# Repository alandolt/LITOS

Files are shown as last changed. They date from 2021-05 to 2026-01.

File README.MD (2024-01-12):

# LITOS - **L**ed **I**llumination **T**ool for **O**ptogenetic **S**timulation

**For more information or if you need any help, please contact us at litosforscience[at]outlook.com.**

The **L**ed **I**llumination **T**ool for **O**ptogenetic **S**timulation (**LITOS**) can be used for the stimulation of cells containing an optogenetic system. A commercially available 32x64 RGB LED matrix is used to illuminate cells placed in various microplate formats (6 well up to 96 wells), petri dishes or cell culture flasks. The control unit for the LED matrix is a custom-built printed circuit board (PCB) containing a screen which shows relevant information during the illumination process. 

During LITOS development, we deliberately focused on user-friendliness. LITOS can be ordered pre-built, thus no complicated assembly process is required. Individual stimulation patterns can be first created in a spreadsheet application, like Microsoft Excel, then they are loaded to LITOS over an easy-to-use interface, accessible as a website hosted on the device itself. Thus, no knowledge of a programming language is needed, and the device can even be operated by nontechnical oriented users. 

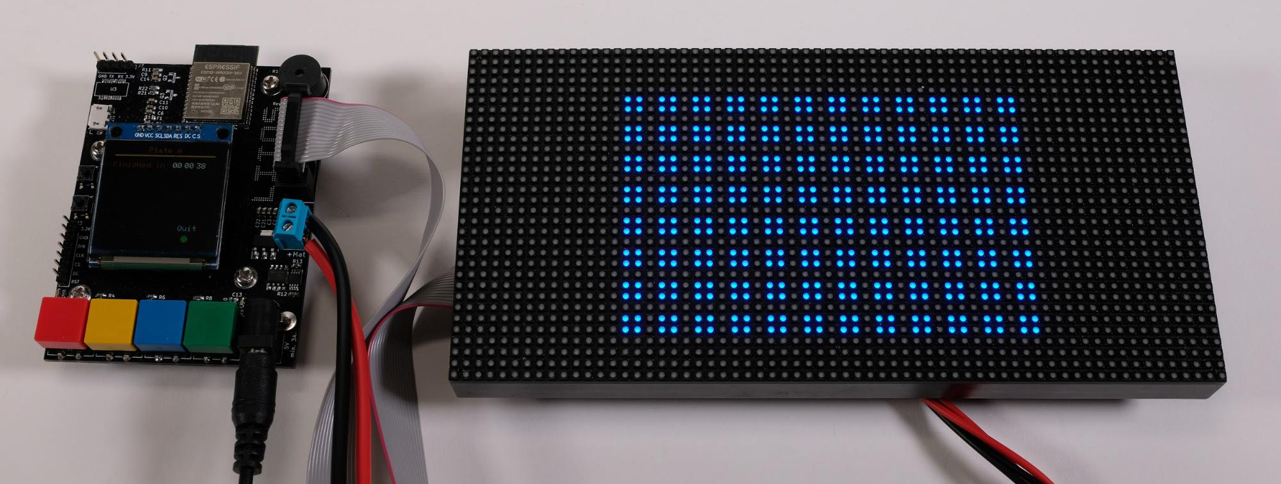
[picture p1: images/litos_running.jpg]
LITOS

*LITOS, an easy-to-use system for optogenetic stimulation*

## Why another device for optogenetic stimulation
Optogenetic methods are powerful tools to assess complex signalling pathways with a high spatial-temporal resolution. However, there is a lack of adequate instrumentation to exploit these methods allowing high-throughput automated experiments. While available commercial devices are often too expensive, published solutions requires programming knowledge or have a complicated assembly process. We presents therefore LITOS, a new emerging tool to render optogenetic methods even accessible to labs with a small budget or non-technical user. Thanks to the easy-to-use–interface no knowledge of a programming language is needed, whereas it is still possible to program complex stimulation patterns. Despite being delivered pre-assembled, LITOS remains significantly cheaper than most of the published and commercially available solutions, costing only $ 150. By using a LED matrix as illumination source, even petri-dishes or cell culture flasks can be stimulated in addition to different formats of microtiter plates.

## Features 
- Easy-to-use graphical user interface to change stimulation patterns for optogenetic experiments. No programming knowledge is required. 
- Stimulation patterns are provided as spreadsheet files (MS Excel, LibreOffice Calc)
- It comes pre-assembled. Neither a 3D printer, nor soldering are required before you can start your experiments. 
- Cells can be placed in well plates (96, 48, 24, 12), petri dishes, or cell culture flasks. 
- Very affordable, only about $150 per device. 

## Getting started

To learn more about LITOS, please read our [paper, published 2022 in scientific reports](https://www.nature.com/articles/s41598-022-17312-x), consult our [github wiki](../../wiki) or checkout the [LITOS - First steps](https://youtu.be/o76gi3OUZvs) video.

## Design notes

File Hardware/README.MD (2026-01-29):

# LITOS Hardware
In case you want to order LITOS directly from a PCB manufacturing service, the folder [*PCB design data*](PCB%20design%20data) contains the needed information (Gerbers file with PCB position file, schematics, and bill of material). Additionally, you can find the raw KiCad PCB layout project under [*LITOS Kicad Rev4.3.zip*](PCB%20design%20data/LITOS%20Kicad%20Rev4.3.zip). 

For the proper alignment of the microtiter plate on the LED matrix the blueprints (for building them with a 3D printer or a CNC machine) for two different masks (one / two microplates) are provided under [*Alignment masks*](Alignment%20masks). The mask for one microplate allows its placement in the middle of the LED matrix, whereas the mask for two plates stocks them horizontally. This allows to stimulate two multiwell plates with one LITOS to further increase through-put. Please note that when using the mask for two plates, the first and last row cannot be illuminated. 

An optional 3D printed case that protects LITOS can be found in the [*3D printed case*](3D%20printed%20case) folder. The case comes in two versions, with or without ventilation holes. Albeit, given that LITOS does not heat up excessively, you can use whichever version you prefer. To minimize overhangs, we recommend you print the case in the orientation it is stored in the .stl file, the open side of the case facing the printer plate. To adjust for under- or overextruding printers, changing the scale of the whole design worked well for us (98%-102%). No support structures were needed with our printer (Creality CR 20 Pro).

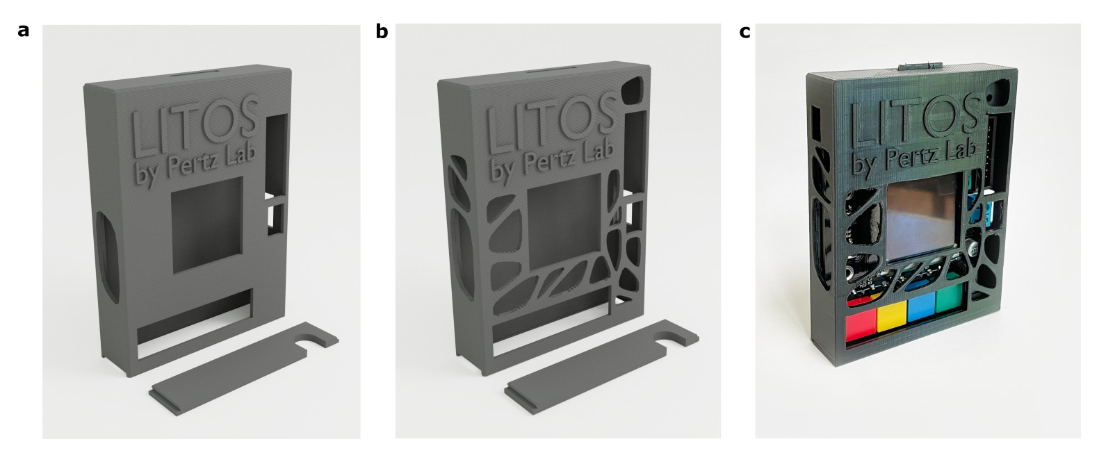
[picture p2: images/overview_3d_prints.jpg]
a) closed design, b) desgin with ventilation holes, c) photo of printed case with ventilation holes


<br>

> **Warning** By default, the source code adapted for revision 4 is used during the programming process. When you are still using an older revision 3 board, you can choose the adapted source code for this version by selecting LITOS_Rev2_Rev3 as build environment in PlatformIO. 

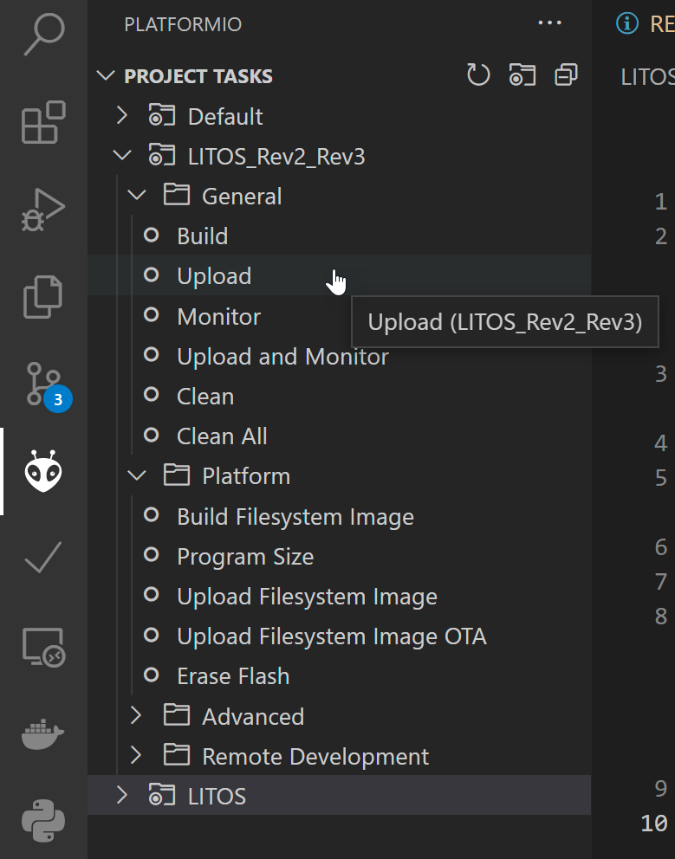
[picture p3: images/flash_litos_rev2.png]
Chose the build environment LITOS_Rev2_Rev3 when you still use an old Rev2 or Rev3 LITOS, else you can directly choose LITOS as build environment


*Chose the build environment LITOS_Rev2_Rev3 when you still use an old Rev2 or Rev3 LITOS, else you can directly choose LITOS as build environment.*

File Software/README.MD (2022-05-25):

# LITOS software

In this folder, you find all the needed files to flash your own LITOS device. For more information check our [wiki](../../../wiki/3.-Setting-up-LITOS'-software).

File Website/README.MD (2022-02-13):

# LITOS configuration website
In this folder, you find the source code of LITOS configuration website. It is based on the [vue-admin-template](https://github.com/PanJiaChen/vue-admin-template) project, which itself is based on [vue.js](https://vuejs.org/). 
After compiling of the JavaScript code, the HTML file is zipped and converted in a C++ file to be served from PROGMEM by the [ESPAsyncWebServer](https://github.com/me-no-dev/ESPAsyncWebServer). 
However, albeit the configuration on LITOS is working without problem, it is currently not possible to compile it by the files provided in this folder, as there is a problem with an outdated dependency. 
We are currently in the process of fixing the error and provide you as soon as possible with an updated, working website version, that you then also can compile yourself.

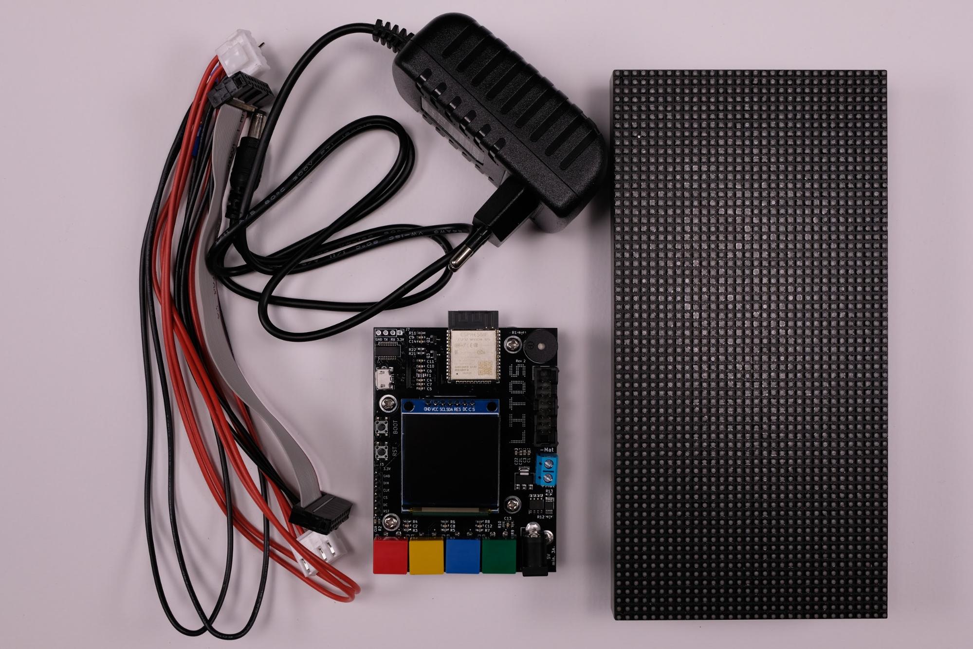
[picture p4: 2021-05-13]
images/litos_overview.jpg

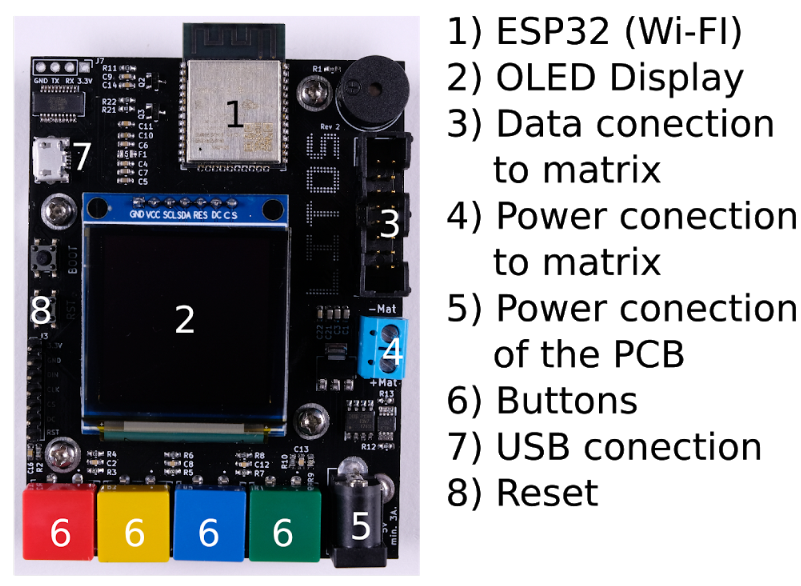
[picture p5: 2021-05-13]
images/pcb_overview.png

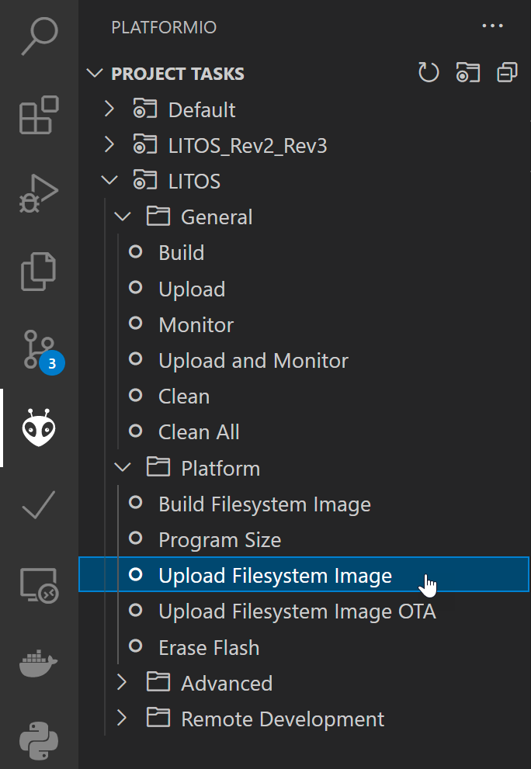
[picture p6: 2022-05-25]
images/flash_file_system.png

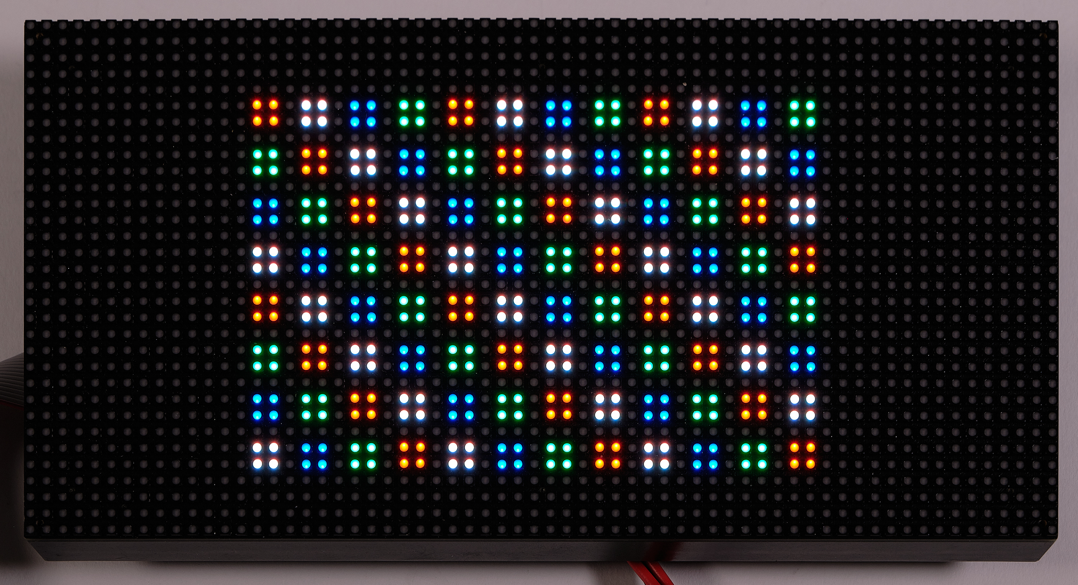
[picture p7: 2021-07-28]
images/LITOS_Muster_3.jpg

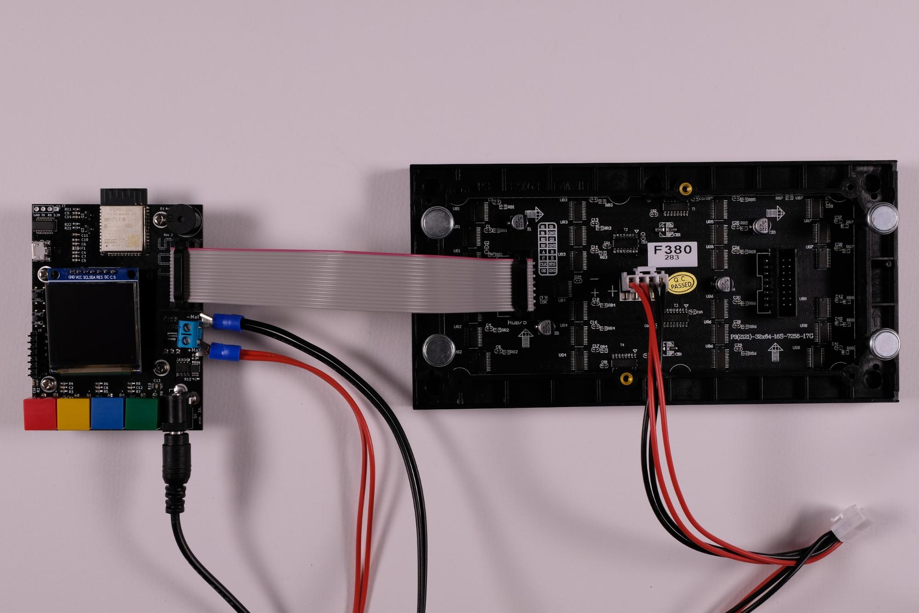
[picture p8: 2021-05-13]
images/litos_back.jpg

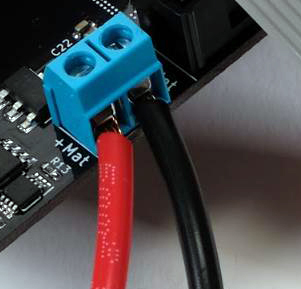
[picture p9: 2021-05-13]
images/power_connector.jpg

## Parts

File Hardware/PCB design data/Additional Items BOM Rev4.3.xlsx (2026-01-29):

LITOS REV 4.3
Additional items
For the BOM please see the .csv, here are only the additionally required items.
Item | Qty | Reference(s) | Value/ Type | Package | Mouser No | Mfr. No | Manufacturer | Description
~~1~~ | ~~1~~ | ~~for SW 3~~ | ~~Switch Cap~~ |  | ~~653-B32-1380 ~~ | ~~B32-1380 ~~ | ~~Omron Electronics ~~ | ~~Switch Bezels / Switch Caps 12MM X 12MM RED CAP ~~
~~2~~ | ~~1~~ | ~~for SW 4~~ | ~~Switch Cap~~ |  | ~~653-B32-1330 ~~ | ~~B32-1330 ~~ | ~~Omron Electronics ~~ | ~~Switch Bezels / Switch Caps 12X12 KEYCAP YELLOW ~~
~~3~~ | ~~1~~ | ~~for SW 5~~ | ~~Switch Cap~~ |  | ~~653-B32-1340 ~~ | ~~B32-1340 ~~ | ~~Omron Electronics ~~ | ~~Switch Bezels / Switch Caps 12X12 KEYCAP BLUE ~~
~~4~~ | ~~1~~ | ~~for SW 6~~ | ~~Switch Cap~~ |  | ~~653-B32-1350 ~~ | ~~B32-1350 ~~ | ~~Omron Electronics ~~ | ~~Switch Bezels / Switch Caps Green 12x12 mm Key Top ~~
 |  | As mouser has the required item not in stock, here another source for all keycaps (all 4 colors included). You can order a 60sets6color set, containing enough keycaps for up to 15 LITOS Rev 4. You can also take keycaps from a local supplier of your choice, the aliexpress links here serves only as a reference. If ordering the keycaps greatly extends the turnaround time (more than 3 days), do not bother to order them and thus ignore position 1-4. Further, if you order from aliexpress, do not put the transparent covers on top of the keycaps. Thanks |  |  |  |  |  | https://www.aliexpress.com/item/32845173329.html?pdp_ext_f=%7B%22sku_id%22%3A%2265174878652%22%7D
5 | 1 | will be mounted on J4 through male/female header interaction | OLED Display Module |  |  |  |  | 1.5 Inch OLED 128x128 Display Color LCD Screen SSD1351 with 2.54mm male headers already soldered in place from your local supplier, for ex. Banggood (currently not in stock, so please see below)
 |  |  |  |  |  |  |  | https://www.banggood.com/1_5-Inch-OLED-128x128-Display-Color-LCD-Screen-SSD1351-Color-OLED-p-1640372.html?rmmds=search&cur_warehouse=CN
 |  |  |  |  |  |  |  | or diymore (or any other local supplier)
 |  |  |  |  |  |  |  | https://aliexpress.com/item/4000380926640.html
 |  |  |  |  |  |  |  | Important: Headers must be already soldered
 |  |  |  |  |  |  |  | also important: you must not take this version of this display (https://www.waveshare.com/wiki/1.5inch_RGB_OLED_Module (as no male headers are present)

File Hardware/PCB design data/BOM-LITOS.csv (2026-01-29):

Comment | Designator | Footprint | LCSC | Quantity
0.1uF | C16,C4,C6 | C_0603_1608Metric_Pad1.05x0.95mm_HandSolder | C14663 | 3
0.1uF/50V | C14,C22,C9 | C_0603_1608Metric_Pad1.05x0.95mm_HandSolder | C14663 | 3
0R | R1,R16 | R_0603_1608Metric_Pad1.05x0.95mm_HandSolder | C21189 | 2
100uF | C1 | CP_Elec_6.3x5.4 | C3001238 | 1
10k | R10,R11,R12,R2,R21,R22,R4,R6,R8 | R_0603_1608Metric_Pad1.05x0.95mm_HandSolder | C25804 | 9
10nF | C12,C13,C2,C8 | C_0603_1608Metric_Pad1.05x0.95mm_HandSolder | C57112 | 4
1k | R3,R5,R7,R9 | R_0603_1608Metric_Pad1.05x0.95mm_HandSolder | C21190 | 4
22uF/10V | C21,C3 | C_0603_1608Metric_Pad1.05x0.95mm_HandSolder | C59461 | 2
4.7k | R13 | R_0603_1608Metric_Pad1.05x0.95mm_HandSolder | C23162 | 1
4.7uF | C10 | C_0603_1608Metric_Pad1.05x0.95mm_HandSolder | C19666 | 1
5.11k | R14,R15 | R_0603_1608Metric_Pad1.05x0.95mm_HandSolder | C23186 | 2
AMS1117-3.3 | U1 | SOT-223-3_TabPin2 | C6186 | 1
B3F-4050 | SW3,SW4,SW5,SW6 | B3F-4050 | C86707 | 4
BSS138PW,115 | Q1 | SOT-323-3_L2.2-W1.3-P1.30-LS2.1-BL | C193366 | 1
Barrel_Jack_MountingPin | J1 | DC-005-5A-2.0 | C381116 | 1
Buzzer | BZ1 | BUZ-SMD_4P-L8.5-W8.5-TL | C189207 | 1
CH340C | U3 | CH340C | C84681 | 1
ESP32-WROOM-32E | U2 | ESP32-WROOM-32E | C701342 | 1
HUB_75 | J2 | B-3000S16P-0110 | C132430 | 1
IRF7416TRPBF | Q4 | IRF7416TRPBF | C3000 | 1
Oled_display_SSD1351_module | J4 | PinSocket_1x07_P2.54mm_Vertical | C2886701 | 1
SS8050-G | Q2,Q3 | SS8050-G | C2150 | 2
SW_Push | SW1,SW2 | PTS647SN50SMTR2LFS | C2799414 | 2
Screw_Terminal_01x02 | J5 | CONN-TH_2P-P7.62_L15.2-W16.7-EX4.2 | C496127 | 1
USB_C_Receptacle_USB2.0 | J6 | USB-C-SMD_MC-311D | C136423 | 1
LOGO | G*** | logo_litos |  | 1

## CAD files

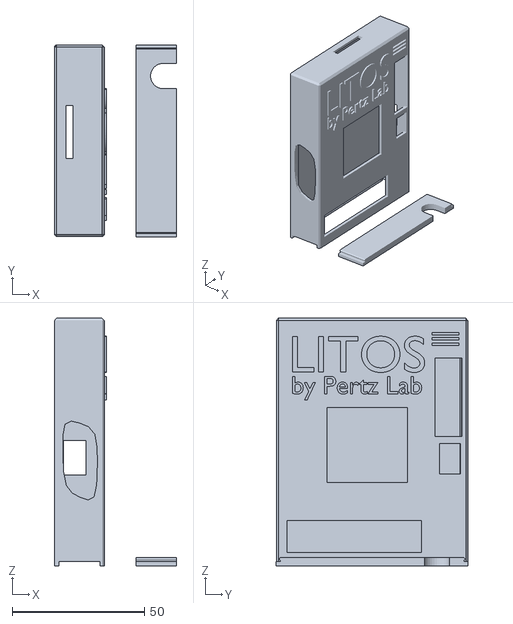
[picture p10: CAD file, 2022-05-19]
Hardware/3D printed case/LITOS_case_rev_4_solid.stl
46.2 x 72.6 x 93.9

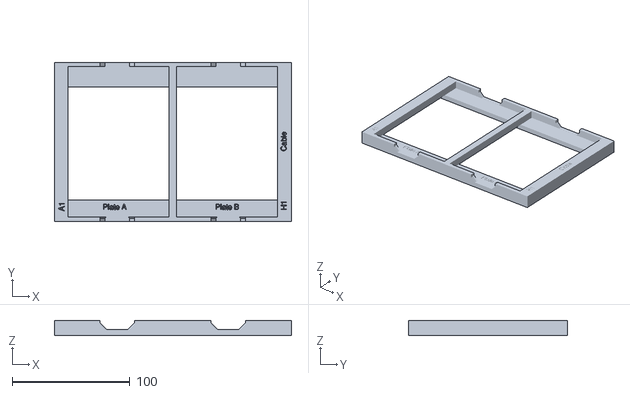
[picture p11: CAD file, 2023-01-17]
Hardware/Alignment masks/mask_two_wellplate.stl
201.6 x 135.2 x 12.4

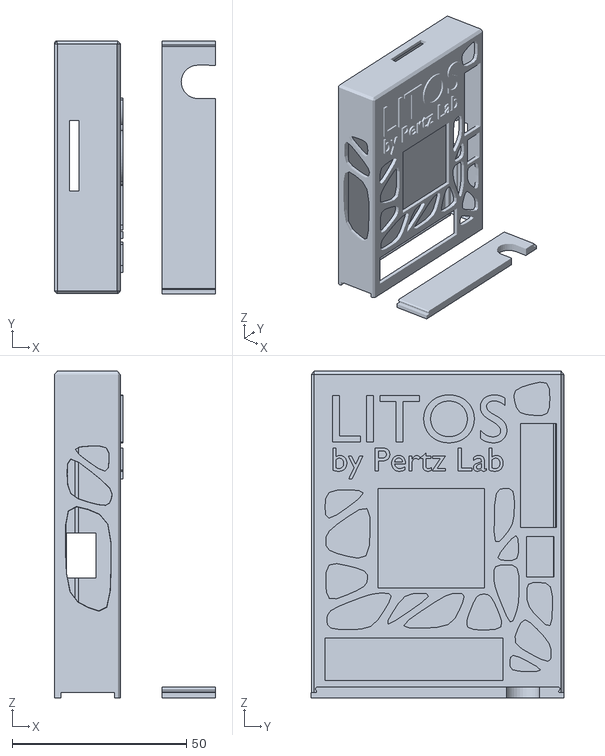
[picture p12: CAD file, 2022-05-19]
Hardware/3D printed case/LITOS_case_rev_4_vents.stl
46.2 x 72.6 x 93.9

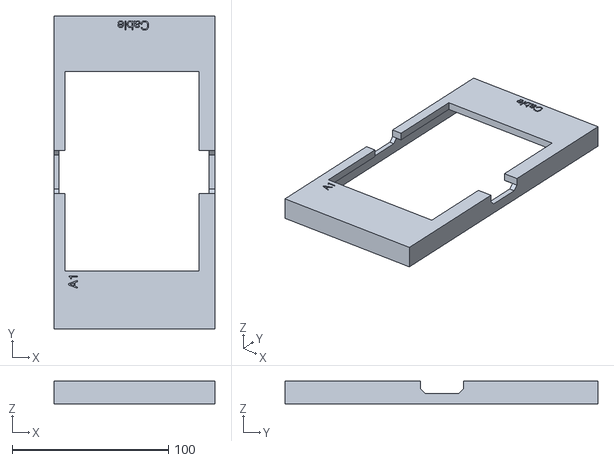
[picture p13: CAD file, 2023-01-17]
Hardware/Alignment masks/mask_one_wellplate.stl
103.1 x 200.2 x 14.7

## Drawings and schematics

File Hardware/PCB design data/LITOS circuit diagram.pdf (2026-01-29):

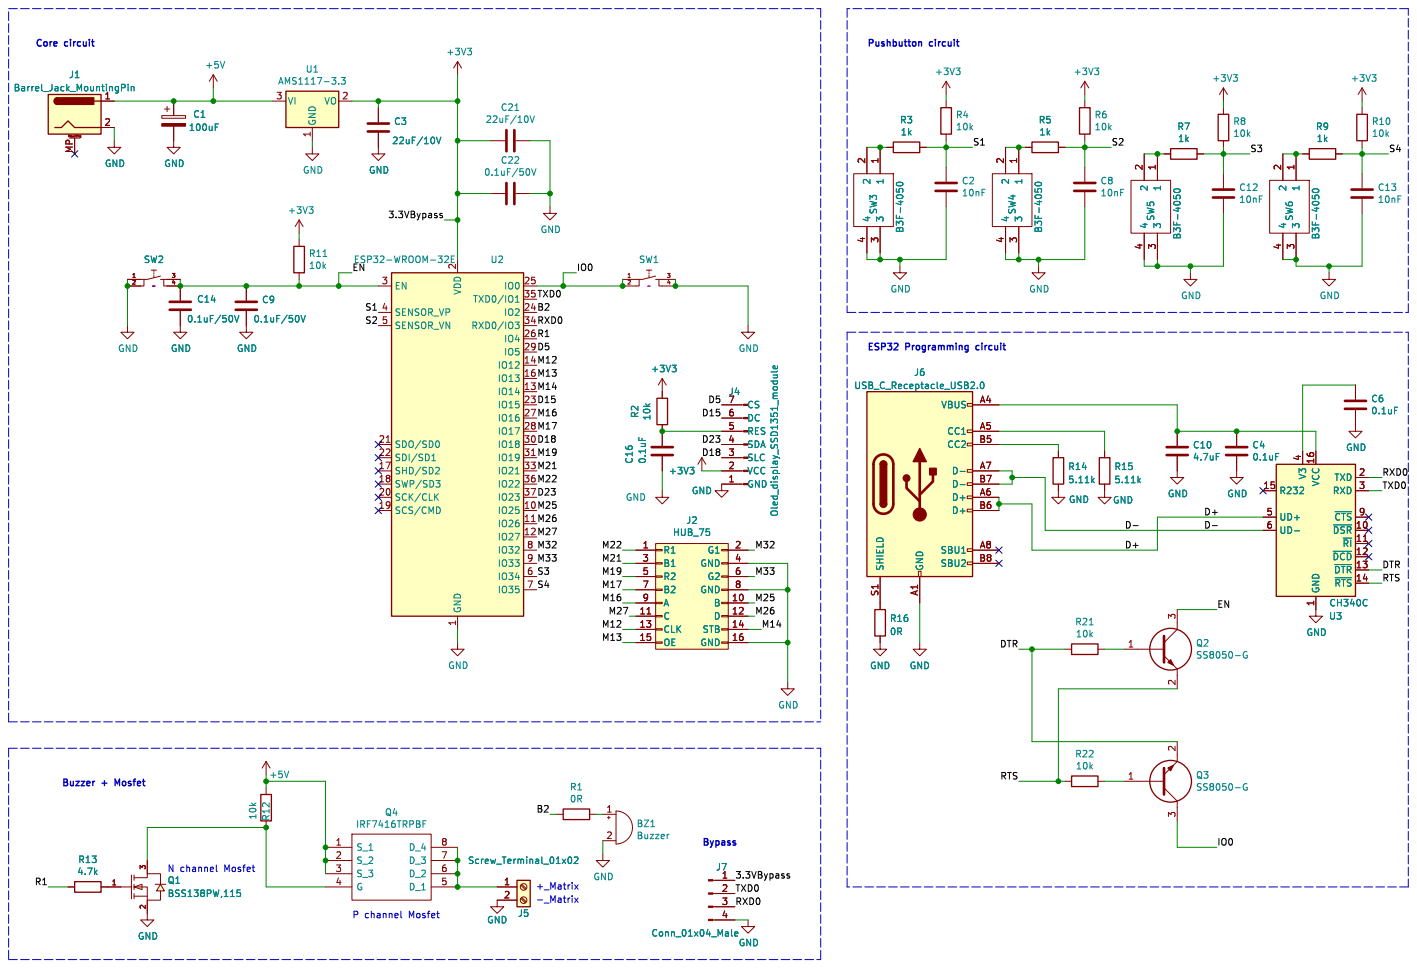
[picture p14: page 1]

1 TXD 2 RXD 3 ~{CTS}9 ~{DSR} 10 ~{RI} 11 ~{DCD} 12 ~{DTR} 13 ~{RTS} 14 GND

1 TXD 2 RXD 3 ~{CTS}9 ~{DSR} 10 ~{RI} 11 ~{DCD} 12 ~{DTR} 13 ~{RTS} 14 U3CH340C

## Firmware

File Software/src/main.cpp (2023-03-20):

/**
 * @file main.cpp
 * @author Alex Landolt
 * @brief Main.cpp file of LITOS, here all the sub librarys and function will be invoked and included. Contains void setup and loop
 * @version 0.3
 * @date 2020-05-25
 */

#include <Arduino.h>
#include <SPIFFS.h>

#include "save_restore_config.h"
#include "wifi_webserver.h"
#include "wellplate.h"
#include "matrix.h"
#include "display.h"
#include "button.h"
#include "buzzer.h"

unsigned long int current_time;
const unsigned long refresh_intervall = 100;
unsigned long last_refresh_time = 0;
bool two_plates_enabled = false;

void setup()
{
	init_matrix_power();
	delay(100);
	Serial.begin(115200);
	SPIFFS.begin(); /// open file system

	config.load_configuration();
	Serial.println(config.get_con_mode());
	Serial.println(config.get_ssid());
	Serial.println(config.get_wlan_password());
	init_wlan();
	delay(100);
	init_webserver();
	delay(200);
	init_display();
	delay(200);
	init_matrix();
	delay(100);

	buzzer.init_buzzer();
	plate_A.wellplate_setup();
	if (config.get_last_wellplate('A') > 100)
	{
		plate_B.wellplate_setup();
		two_plates_enabled = true;
	}
}
void loop()
{
	current_time = millis();

	switch (screen)
	{
	case home_screen:
		if (button_1.pressed()) /// both well plates A + B will be started
		{
			screen = status_A_B_screen;
			plate_A.begin(current_time);
			plate_B.begin(current_time);
			draw_status_screen();
		}
		if (button_2.pressed()) /// only A will be started
		{
			screen = status_A_screen;
			plate_A.begin(current_time);
			draw_status_screen();
		}
		if (button_3.pressed()) /// only B will be started
		{
			screen = status_B_screen;
			plate_B.begin(current_time);
			draw_status_screen();
		}
		if (button_4.pressed()) // show test screen where outlines can be marked
		{
			screen = test_screen;
			draw_test_screen();
		}
		break;
	case home_screen_one:
		if (button_2.pressed()) /// only A will be started
		{
			screen = status_A_screen;
			plate_A.begin(current_time);
			draw_status_screen();
		}
		if (button_4.pressed()) // show test screen where outlines can be marked
		{
			screen = test_screen;
			draw_test_screen();
		}
		break;
	case status_A_screen: /// A is currently running
		if (QUIT_ON_RED)
		{
			if (button_1.pressed()) /// abort and go back to home
			{
				plate_A.abort_program();
				screen = home_screen;
				draw_home();
			}
		}
		else
		{
			if (button_4.pressed()) /// abort and go back to home
			{
				plate_A.abort_program();
				screen = home_screen;
				draw_home();
			}
		}
		break;
	case status_B_screen: /// B is currently running
		if (QUIT_ON_RED)
		{
			if (button_1.pressed()) /// abort and go back to home
			{
				plate_B.abort_program();
				screen = home_screen;
				draw_home();
			}
		}
		else
		{
			if (button_4.pressed()) /// abort and go back to home
			{
				plate_B.abort_program();
				screen = home_screen;
				draw_home();
			}
		}
		break;

	case status_A_B_screen: /// A and B are running simultanously
		if (QUIT_ON_RED)
		{
			if (button_1.pressed()) /// abort and go back to home
			{
				plate_A.abort_program();
				plate_A.abort_program();
				screen = home_screen;
				draw_home();
			}
		}
		else
		{
			if (button_4.pressed()) /// abort and go back to home
			{
				plate_A.abort_program();
				plate_A.abort_program();
				screen = home_screen;
				draw_home();
			}
		}
		break;

	case test_screen:
		if (button_1.pressed())
		{
			plate_A.mark_outlines();
			if (two_plates_enabled)
			{
				plate_B.mark_outlines();
			}
		}
		if (button_2.pressed())
		{
			plate_A.mark_well();
			if (two_plates_enabled)
			{
				plate_B.mark_well();
			}
		}
		if (button_4.pressed())
		{
			plate_A.reset_mark();
			plate_B.reset_mark();
			ref_backgroundLayer().clearScreen();
			draw_home();
		}
		break;
	default:
		break;
	}

	if (plate_A.check(current_time) | plate_B.check(current_time)) /// power on / power off Matrix through MOSFET high/low pin
	{
		matrix_on();
	}
	else
	{
		matrix_off();
	}

	if (current_time - last_refresh_time >= refresh_intervall)
	{
		update_status_screen(); /// updates the status screens of the OLED display
		messages.update(current_time);
		buzzer.check_beep(current_time); // check if a beep has been requested by another part of the programm
		last_refresh_time += refresh_intervall;
	}
	dns_server_next_request();
	delay(5);
}

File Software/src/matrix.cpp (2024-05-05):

/**
 * @file matrix.cpp
 * @author Alex Landolt 
 * @brief C file containing functions needed for controlling the LED matrix and the MOSFET
 * @version 0.3
 * @date 2020-05-25
 */
#include "matrix.h"

RGB64x32MatrixPanel_I2S_DMA backgroundLayer;

#define R1 GPIO_NUM_22
#define G1 GPIO_NUM_32
#define BL1 GPIO_NUM_21
#define R2 GPIO_NUM_19
#define G2 GPIO_NUM_33
#define BL2 GPIO_NUM_17

#define CH_A GPIO_NUM_16
#define CH_B GPIO_NUM_25
#define CH_C GPIO_NUM_27
#define CH_D GPIO_NUM_26
#define CH_E -1

#define LAT GPIO_NUM_14
#define OE GPIO_NUM_13
#define CLK GPIO_NUM_12

int sig_data_base = I2S1O_DATA_OUT8_IDX;
int sig_clk = I2S1O_WS_OUT_IDX;
gpio_num_t gpio_pins_def[16] = {R1, G1, BL1, R2, G2, BL2, LAT, OE, CH_A, CH_B, CH_C, CH_D};

const byte led_matrix_mosfet = 4; /// pin where the MOSFET is located
static bool is_matrix_on;

/**
 * @brief Used to generate reference to LED matrix, as so we can control it in the wellplate part of LITOS code
 * 
 * @return RGB64x32MatrixPanel_I2S_DMA&, that is nothing more than a reference to the LED matrix
 */
RGB64x32MatrixPanel_I2S_DMA &ref_backgroundLayer()
{
    return backgroundLayer;
}

/**
 * @brief called in void setup to initialize matrix
 * 
 */
void init_matrix()
{
    //matrix_on();
    digitalWrite(led_matrix_mosfet, HIGH);
    reset_panel();
    digitalWrite(led_matrix_mosfet, LOW);

    backgroundLayer.setPanelBrightness(60);
    backgroundLayer.begin(R1, G1, BL1, R2, G2, BL2, CH_A, CH_B, CH_C, CH_D, CH_E, LAT, OE, CLK);
    digitalWrite(led_matrix_mosfet, HIGH);
    matrix_off(); /// helper function to cut off data lines
}

void init_matrix_power()
{
    pinMode(led_matrix_mosfet, OUTPUT); /// initialize MOSFET pin
    is_matrix_on = true;
    matrix_off();
}

/**
 * @brief helper function to cut off data lines and power through MOSFET and internal pull down resistors 
 * 
 */
void matrix_off()
{
    if (is_matrix_on)
    {
        backgroundLayer.fillScreen(0x0000);
        digitalWrite(led_matrix_mosfet, LOW);
        delay(20);
        sleep_matrix(gpio_pins_def);
        is_matrix_on = false;
    }
}
/**
 * @brief activate matrix by supplying power through internal MOSFET 
 * 
 */
void matrix_on()
{
    if (!is_matrix_on)
    {
        wake_up_matrix(gpio_pins_def);
        digitalWrite(led_matrix_mosfet, HIGH);
        is_matrix_on = true;
    }
}

void gpio_setup_out(gpio_num_t gpio, int sig)
{
    PIN_FUNC_SELECT(GPIO_PIN_MUX_REG[gpio], PIN_FUNC_GPIO);
    gpio_set_direction(gpio, GPIO_MODE_OUTPUT);
    gpio_matrix_out(gpio, sig, false, false);
}

void sleep_matrix(gpio_num_t *gpio_pins)
{
    for (int x = 0; x < 12; x++)
    {
        gpio_setup_out(gpio_pins[x], 0x100);
    }
    gpio_setup_out(CLK, 0x100);
}

void wake_up_matrix(gpio_num_t *gpio_pins)
{
    for (int x = 0; x < 12; x++)
    {
        gpio_setup_out(gpio_pins[x], sig_data_base + x);
    }
    gpio_setup_out(CLK, sig_clk);
}

void reset_panel()
{
    int MaxLed = 64;

    int C12[16] = {0, 1, 1, 1, 1, 1, 1, 1, 1, 1, 1, 1, 1, 1, 1, 1};
    int C13[16] = {0, 0, 0, 0, 0, 0, 0, 0, 0, 1, 0, 0, 0, 0, 0, 0};

    pinMode(R1, OUTPUT);
    pinMode(G1, OUTPUT);
    pinMode(BL1, OUTPUT);
    pinMode(R2, OUTPUT);
    pinMode(G2, OUTPUT);
    pinMode(BL2, OUTPUT);
    pinMode(CH_A, OUTPUT);
    pinMode(CH_B, OUTPUT);
    pinMode(CH_C, OUTPUT);
    pinMode(CH_D, OUTPUT);
    pinMode(CH_E, OUTPUT);
    pinMode(CLK, OUTPUT);
    pinMode(LAT, OUTPUT);
    pinMode(OE, OUTPUT);

    // Send Data to control register 11
    digitalWrite(OE, HIGH); // Display reset
    digitalWrite(LAT, LOW);
    digitalWrite(CLK, LOW);
    for (int l = 0; l < MaxLed; l++)
    {
        int y = l % 16;
        digitalWrite(R1, LOW);
        digitalWrite(G1, LOW);
        digitalWrite(BL1, LOW);
        digitalWrite(R2, LOW);
        digitalWrite(G2, LOW);
        digitalWrite(BL2, LOW);
        if (C12[y] == 1)
        {
            digitalWrite(R1, HIGH);
            digitalWrite(G1, HIGH);
            digitalWrite(BL1, HIGH);
            digitalWrite(R2, HIGH);
            digitalWrite(G2, HIGH);
            digitalWrite(BL2, HIGH);
        }
        if (l > MaxLed - 12)
        {
            digitalWrite(LAT, HIGH);
        }
        else
        {
            digitalWrite(LAT, LOW);
        }
        digitalWrite(CLK, HIGH);
        digitalWrite(CLK, LOW);
    }
    digitalWrite(LAT, LOW);
    digitalWrite(CLK, LOW);
    // Send Data to control register 12
    for (int l = 0; l < MaxLed; l++)
    {
        int y = l % 16;
        digitalWrite(R1, LOW);
        digitalWrite(G1, LOW);
        digitalWrite(BL1, LOW);
        digitalWrite(R2, LOW);
        digitalWrite(G2, LOW);
        digitalWrite(BL2, LOW);
        if (C13[y] == 1)
        {
            digitalWrite(R1, HIGH);
            digitalWrite(G1, HIGH);
            digitalWrite(BL1, HIGH);
            digitalWrite(R2, HIGH);
            digitalWrite(G2, HIGH);
            digitalWrite(BL2, HIGH);
        }
        if (l > MaxLed - 13)
        {
            digitalWrite(LAT, HIGH);
        }
        else
        {
            digitalWrite(LAT, LOW);
        }
        digitalWrite(CLK, HIGH);
        digitalWrite(CLK, LOW);
    }
    digitalWrite(LAT, LOW);
    digitalWrite(CLK, LOW);
}

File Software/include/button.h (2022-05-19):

/**
 * @file button.h
 * @author Alex Landolt
 * @brief Header file for button class. Handles pushbutton with Software debounce through checking them multiple times before triggering an action.
 * @version 0.3
 * @date 2020-05-25
 */

#ifndef BUTTON_H
#define BUTTON_H

#define PIN_BUTTON_1 36
#define PIN_BUTTON_2 39
#define PIN_BUTTON_3 34
#define PIN_BUTTON_4 35

#ifdef LITOS_REV_2
#undef PIN_BUTTON_1
#define PIN_BUTTON_1 35
#undef PIN_BUTTON_2
#define PIN_BUTTON_2 34
#undef PIN_BUTTON_3
#define PIN_BUTTON_3 39
#undef PIN_BUTTON_4
#define PIN_BUTTON_4 36
#endif

#include <Arduino.h>

/**
 * @brief Class to register and handle push button press with Software debounce
 *
 */
class Button
{
private:
    byte _button, _state, _lastState, _reading;
    unsigned int _count;
    unsigned long _delay, _last;
    boolean _wait;
    bool _1st_press;
    void Button_u(byte &button_pin); /// underlaying function used for initialization

public:
    Button(byte button_pin);                      /// constructor to create Button object on specific pin of ESP32
    Button(byte button_pin, unsigned long delay); /// Button object with custom debounce delay

    bool pressed();       /// returns the debounced button state: LOW or HIGH.
    unsigned int count(); /// Returns the number of times the button was pressed.
    void resetCount();    /// Resets the button count number.
};

extern Button button_1; /// Declaration of Buttons 1-4 of LITOS
extern Button button_2;
extern Button button_3;
extern Button button_4;

#endif

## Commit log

2020-04-04 same status as first release, felis silvestris
    [demo.csv]
2020-04-20 rename (remove init_)
    [demo.csv]
2020-04-22 two_wellplates now_working
    [plate_A.csv, plate_B.csv]
2020-05-06 bug fix_websocket crashed in get file list
    [LITOS_proof.csv, MCF10A_Exp1.csv, demo.csv, pertz_lab_Exp2.csv]
2020-07-22 rect circle nun einstellig, Korr webserver, partition
    [no_ota.csv]
2020-09-07 1.3.0: Outline function
    Implementation of an outline function which marks the outlines of a microplate. Additionally the corner wells can be marked to place the microplate correctly on the LED RGB Matrix. Over the website i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
2021-03-15 branch with DMA LED matrix library
    This branch uses the DMA LED matrix from
    https://github.com/mrfaptastic/ESP32-RGB64x32MatrixPanel-I2S-DMA/
    It uses DMA memory instead of heap allocation.
    In theory it uses less CPU.
    As the underlaying API is different (Adafruit GFX instead of smartmatrix), all function calls manipulating the drawn forms in wellplate.cpp and matrix.cpp were changed. Additionally, as the radius is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
2021-07-27 Housekeeping: Addition of README.MD and manual
    [large_spiffs_16MB.csv, no_ota.csv]
2022-02-01 Addition of masks for 3D printer
    [1Plate_cover.dxf, 1Plate_cover_original.dxf, 2Plate_cover.dxf, 2Plate_cover_original.dxf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]
2022-02-02 Move everything to software related to software folder
    [LITOS_proof.csv, MCF10A_Exp1.csv, large_spiffs_16MB.csv, no_ota.csv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]
2022-02-13 Addition of PCB schematics
    [LITOS_v3 BOM.xlsx, LITOS_v3-B_Cu.gbl, LITOS_v3-B_Mask.gbs, LITOS_v3-B_SilkS.gbo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]
2022-03-17 added example patterns
    [Demo.csv, Demo2_loops.csv, Demo3_colors.csv, Demo4_shapes.csv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]
2022-03-17 add new demo file
    [Demo.csv]
2022-03-17 move files to folder example patterns
    [Demo.csv, Demo2_loops.csv, Demo3_colors.csv, Demo4_shapes.csv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]
2022-04-07 Pre-release of hardware revision 4 of LITOS PCB
    - USB flashing error present in rev 3 got fixed
    - Software mostly interchangable between rev 3 and 4.
    - PCB revision gets currently tested
    - For more information, see Redme in hardware folder.
    [LITOS_v3 BOM.xlsx, LITOS_v3-B_Cu.gbl, LITOS_v3-B_Mask.gbs, LITOS_v3-B_SilkS.gbo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]
2022-04-16 Bugfix for PCB Pre-release Rev 4
    - Depending on the micro USB, you have chosen for the assembly, it is possible that the micro USB connector flange is placed on top of the board, instead being feely besides the board. By placing the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
2022-05-13 Compillation did not work anymore on new esp32 core due to ESP32 Async webserver library.
    Fixed by taken this library directly from git repository instead of platformio repo
2022-05-18 Change to espressif32 3.5.0 as rebootloop when flashing with espressif32 4.2.0 framework
2022-05-19 Adapt Platformio.ini and code to be able to compile LITOS source code for both board revisions, Rev 2 and Rev4.
    The board revisions 2 and 4 are distinguished by different button mappings. Further, some of the Rev2 boards had problems with a spontanous triggering of the quit (green) button. Thus, the exit of th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
    Pin definitions for the baords can be found in button.h
2022-05-19 LITOS Release 2.0 with hardware revision 4
    Compared to the prerelease of revision 4, C5 had been removed. It seems that the capacitors attached to the buttons of RST and BOOT lock the ESP32 into the bootloader when doing a cold start as both 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
    Further the board was shortened by 1 mm, as the linked micro-USB connector could not be soldered flat on the board, as some overhang was needed for the micro-USB connector.
    To ensure compatibility with LITOS Rev2 and Rev3, we added a LITOS_Rev2_Rev3 build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
    [1Plate_cover.dxf, 1Plate_cover_original.dxf, 2Plate_cover.dxf, 2Plate_cover_original.dxf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]
2022-05-24 Bugfix LED x/y parsing
    It is now possible agin to illuminate individual LEDs by using the LED_x_y what command.
2022-05-24 Bugfix Rectangle + Circle parsing
    [Demo4_shapes.csv]
2022-05-30 added 3d printing details (#1)
    * Update README.MD with 3d printer information
    - Added details for 3d printing process
    - Changed to new warning block-quote (github.com/github/feedback/discussions/16925)
    * Figure that shows 3d prints
    - solid model
    - model with vents
    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
2022-12-18 compatibility with Rev 4.3
    [8MB.csv]
2026-01-29 Adding PCB Hardware Revision 4.3
    - USB-C instead of microUSB connection
    - Update MOSFET circuit, as original MOSFET was out of production
    - Smaller Fixes in hardware design
    [Additional Items BOM Rev4.3.xlsx, BOM-LITOS.csv, CPL-LITOS.csv, LITOS_v4 BOM.xlsx]
